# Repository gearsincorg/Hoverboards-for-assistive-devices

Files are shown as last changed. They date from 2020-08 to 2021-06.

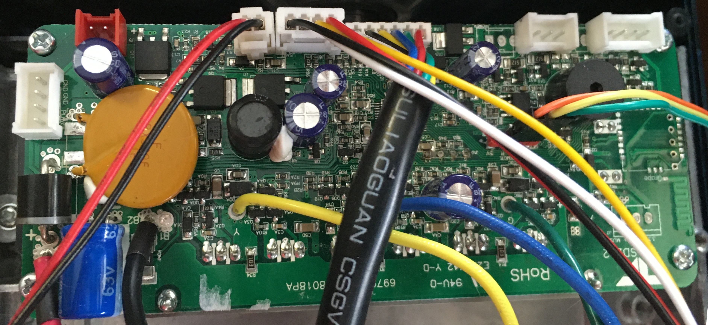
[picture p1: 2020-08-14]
Hoverboard/Documents/MasterBoard.jpg

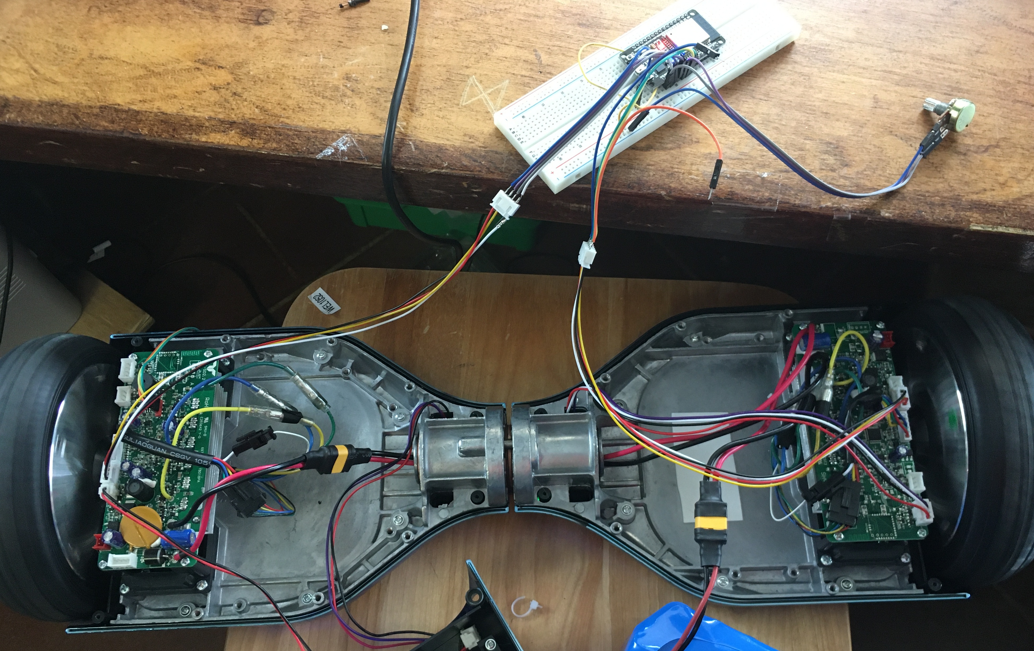
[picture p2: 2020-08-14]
Hoverboard/Documents/Prototype1.jpg

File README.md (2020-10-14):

### Hoverboards for Assistive Devices (HAD) 
By: Phil Malone

Project page:  https://hackaday.io/project/170932-hoverboards-for-assistive-devices

### Purpose:
The HAD project goal is to enable Hoverboards, or Hoverboard drive components to be re-purposed to provide low-cost mobility for assistive devices.

### Components:
The following components are part of this project:

Hoverboard  This is Hoverboard firmware that supports HUGS (Hoverboard Universal Gateway System).  HUGS is new firmware that is loaded into a hoverboard to replace the tilt-based drive system with a command driven velocity system.  HUGS provides a documented command/response protocol whereby commands can be issued to single or dual drive conteollers.

BluJoy-PCB (Bluetooth Joystick PCB).  BluJoy-PCB is a custom two-part Circuit board with PIC microcontroller and two Bluetooth module.  Once sepparated, the two boards enables the Hoverboard to be controlled by a joystick, over a dedicated Bluetooth interface.  

BluJoy.X (Bluetooth Joystick Firmware). BluJoy.X is a custom MPLAB.X program loaded into the PIC processor on the BluJoy PCB.  It performs automatic Bluetooth pairing, and joystick command transmission.  The firmware currently supports microswitch based joysticks, but will be augmented for Potentiometer based joysticks soon.

HUGS-ESP32 This is developmental code for an ESP32 Dev-kit that was used to test and evaluate the HUGS firmware on the Hoverboard. It connects to a wired joystick to generate commands for both Motor Controllers.  It has been superceeded by the BluJoy PIC firmware which communicates through a single Serial port on the Master Motor Controller.

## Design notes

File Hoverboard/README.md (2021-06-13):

### Hoverboard Utility Gateway System (HUGS).

Based on: Hoverboard-Firmware-Hack-Gen2

Hackaday Project Page: https://hackaday.io/project/170932-hoverboards-for-assistive-devices

### Purpose:
The HUGS project goal is to enable Hoverboards, or Hoverboard drive components to be re-purposed to provide low-cost mobility to other systems, such as assistive devices for the disabled, general purpose robots or other labor saving devices.
To implement this goal, new code will be developed and installed in existing hoverboards, to provide a generic purpose control protocol.  This protocol will be used by external devices to run one or more “hoverboard” type wheels.  

### Updated to use new Giga Device Libraries: (3.2) and latest KEIL release (as of 6/13/2021)

### Latest release:
A major modification to the base control strategy was adding several different motor control methods.

The basic method is a simple PWM power control where the the user requests a PWM level from 0 to 1000 and the comutation happens as required by the current sensed position.  The resulting speed is an open loop response.

The next method was a closed loop response using the resultant phase transition speed as feedback. A Feed forward control loop with proportional and integral gain was created to regulate the resulting speed.  Control input is an actual linear speed in the +/- 5MPS range, expressed in mmPS.

The third method is a low speed closed loop mode that uses a sinusoidal stepper motor sequence to drive the commutation at a fixed rate, depending on the requested speed.  The method optains higgly accurate speeds at rates less than about 200 mmPS.

The fourth and final mode is a hybrid of the last two which switches automatically between the low speed stepper mode and the PID control mode.

### Background:
The popular “Hoverboard” toy uses a somewhat unique drive system.  A powerful brushless DC motor has been integrated inside each of the small rubber wheels, and paired with a low cost motor controller.  This mechanical/electrical combination provides a compact drive system that produce precise motions, under considerable load, for relatively low cost.

Through reverse engineering the controller electronics and firmware, code is now available which can be modified to provide alternative operation of the drive system (no longer tied to a tilt-and-drive control system).

The goal of HUGS is to reprogram the motor controller to accept external control commands, and return wheel status information.  HUGS will permit individual wheels to be commanded to run at set speeds, and to move to specified positions.  Current speed and position information will be returned.
By providing an open control protocol, other groups can develop their own high level control logic to run the drive wheels for a myriad of applications.

This repo contains open source firmware that has been deveoped and tested on HOVER-1 Ultra Hoverboard

---

#### Hardware
My initial Hoverboard purchase was the Hover-1 Ultra.  I wanted to do the work on a board that could be purchased by name.
I chose this model because it looked like the company had several models and was likely to be a more reliable vendor than most "direct from China" vendors.

Ultimately my choice backfired on me because instead of the more common single board controller, this unit had two boards (one master and one slave).  So I had to work from a more limited development set of Gen2 hoverboard.

My most upsetting discovery was that when I was all done, I purchased a different model (Maverick vs Ultra) from the same supllier, and discovered that the Ultra code does not translate.   

Since I'm realy not able to reverse engineer this new hardware, this my be a throw-away hoverboard.

So "For the record" everything here has been developed on the Hover-1 Ultra unit, and pictures of the controller boards are in the Documentation folder of this repo.

The HOVER-1 Ultra has two sepparate motor controller boards, usually configured as a master and a slave with a USART Serial port passing commands and data back and forth.

There is a sets of pads that can be used to program the processor using a ST-Link/V2.

There is also a set of pads that can be used for a remote monitor /control port.

---

#### Flashing

The firmware is built with Keil (free up to 32KByte). 
To build the firmware, open the Keil project file (includes in repository).

- If the controller boards contain the original firmware, they will need to be unlocked. To do this, use the STM32 ST-LINK Utility.
- To flash the STM32, use the STM32 ST-LINK Utility, or use Keil and run the code in debug mode, which will download the code first.
- Hold the powerbutton while flashing the firmware, as the controller releases the power latch and switches itself off during flashing

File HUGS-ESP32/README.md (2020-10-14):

# HUGS Human Machine Interface (HMI) ESP32 module.  (Superceeded)

This code is used to program an ESP32 DEVKIT board to send command packets to a Hoverboard (dual controller type) that has been reprogrammed to communicate using the HUGS Protocol.

The code is built using the Espressif-IDF environment.

This code was originally intended to be used as the primary way to interface to a "dual controller" type hoverboard because the ESP32 can drive two serial ports, as well as the programming interface.
This concept was used to implement a wired joystick controller. The code is fully operation, but it will probably not be further developed.  See below. 

Unfortunately, this approach did not lend itself to a simple wireless joystick interface.

To provide a wireless control (joystick) interface, the HUGs protocol was extended to permit a single serial command to be sent to the master motor controller, which would then forward the appropriate components to the slave motor controller using the standard serial cable that is part of the split controller system.
This means that both drives to be controlled using a single serial interface.  This approach enables a simpler uController to be used to "drive" the Hoverboard, and also permits a simple Bluetooth-Serial module to be used to create a wireless interface.

This approach was developed into the BluJoy controller that is also contained in this repo. This design will ultimately replace both the wireless and wires control approach.

For additional information, refer to the Hoverboard Utility Gateway System repo.

https://github.com/gearsincorg/Hoverboard_Utility_Gateway_System

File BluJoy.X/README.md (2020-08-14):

### Hoverboards for Assistive Devices (HAD) 
By: Phil Malone

BluJoy.X is a (Microchip) MPLAB firmware project.
It was created using MPLAB X IDE Version 5.4
It's written in C8 and it makes use of the V3 Code Configurator Module.

The code runs on a PIC16LF18446 processor.  
The '18446 was chosen because it has a serial USART with Configurable Port Pins, and a small quantity of EEPROM memory for storing configuration settings.

I use a PicKit3 to program the processor once it's mounted to the PCB.  

The Firmware is written to run on the BluJoy-PCB which is included as part of this repository.

The code operates in two main modes:

- RUN.	In this mode, the code determines the current joystic configuration from EEPROM, and applies the appropriate speed profiles to the Joystick inputs.  Every 50 mSec, new Axial and Yaw velocities are calculated and sent to the Hoverboard via Bluetooth.

- SETUP.  In this mode, the code reads the device ID's of the two attached Bluetooth modules, and used this information to configure each module to auto-connect with the other module.

To enter the SETUP mode, press and hold both buttons on the PCB for 4 seconds.

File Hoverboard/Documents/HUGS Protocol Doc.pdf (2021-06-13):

HUGS Protocol definition

Revision | Date | Description
Revision | 1.0 | 4/13/2020 Original
2.0 | 5/8/2020 Change to Little Endian.Change to metric speeds. (mm/s)
2.1 | 5/14/2020 Add new Motion Response with Velocity, Position, Power.
2.2 | 7/20/2020 Remove any response for NOR (no response)
3.0 | 1/1/2021 Added new Dual commands to be used by the single debug port on the master.

Note: HUGS uses a binary format, rather than an ASCII character format, so it is not directly printable. Note: All HUGS multi-byte values are sent as little-endian. That is, the LSB is sent first and the MSB sent last.

0 | 1 | 2 | 3 | 4 | 5 | L+4 | L+5 | L+6 | L+7
Send/Rec | BOM | LEN | DEST/SEQ | CMD_ID | RSP_ID | EOM
BOM | Beginning Of Message Character: | Slash | "/"
LEN | Length of variable Data. 0 - 0xF7
DEST/SEQ | LSN (Lower 4 bits) TARGET Identifier. 0-15 | 0x0 = HOST, 0xF = ALL
MSN (Upper 4 bits) Message Sequence. Cycles through 0-15
CMD_ID | On a command, this will be the required action. Indicates how to interpret variable data section
On a response, the CMD_ID will be RSP
RSP_ID | On a command, this is the required Response: Indicates what data should be returned.
On a response, theRSP_ID will be the type of data bing returned in the response.
DATA | Variable number of data bytes . Length defined by LEN parameter
CRC | 16-bit Cyclic Redundancey Check of Bytes 0 to L+4
EOM | End Of Message character: | | Newline | \n 0x0A
Command IDs | Name | Value | LEN
No Operation | NOP | 0x00 | 0
Response | RSP | 0x01 | 0
Reset Pos | RES | 0x02 | 0
Enable | ENA | 0x03 | 0
Disable | DIS | 0x04 | 0
Set Power | POW | 0x05 | 2 | Def 0
Set Speed | SPE | 0x06 | 2 | mm/s (+/- 5000) | Def 0
Set ABS Pos | ABS | 0x07 | 2 | mm (+/- 32767) | Def 0
Set Rel Pos | REL | 0x08 | 2 | mm (+/- 32767) | Def 0
Set Watchdog | DOG | 0x09 | 2 | mS (0-65535) | Def 1000
Set Mode | MOD | 0x0A | 2 | 0,1,2,3 | 0-255mmPs | Def 1,250 | 0=PID,1=STEPPER,2=Hybrid
Set Dual Speed | DSPE | 0x86 | 4 | mm/s (+/- 5000) FW | deg/s (+/- 1425) CW | +=forward, +=clockwise
Power Down | XXX | 0xFF | 0
Response ID | Name | Value | LEN | Data
No Response | NOR | 0x00 | 0
Motion | SMOT | 0x01 | 9 | STATUS | mm/s (+/- 6000) | mm (+/- 2,147,483,648)
Power | SPOW | 0x02 | 3 | STATUS
Velocity | SSPE | 0x03 | 3 | STATUS | mm/s (+/- 6000)
Position | SPOS | 0x04 | 5 | STATUS | mm (+/- 2,147,483,648)
Voltage | SVOL | 0x05 | 3 | STATUS | mV (0-65535)
Current | SAMP | 0x06 | 3 | STATUS | mA (0 65535)
Watchdog | SDOG | 0x07 | 3 | STATUS | mS (0 65535)
PID | SFPI | 0x09 | 7 | STATUS
DualMotion | DSMOT | 0x81 | 13 | STATUS | mm/s (+/- 5000) FW | deg/s (+/- 1425) CW | mm (+/- 2,147,483,648) LEFT WHEEL
Stopped | STOP | 0xFF | 1 | STATUS
STATUS | Bit | 7 | 6 | 5 | 4 | 3 | 2 | 1 | 0
| | | | | | MOD 1 | MOD 0 | Enabled | ESTOP
DATA: LEN Bytes | CRC

+/-1000

+/-1000

F Output | P Output | I Ouput

+/-1000

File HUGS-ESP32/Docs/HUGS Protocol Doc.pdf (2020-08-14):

HUGS Protocol definition

Revision | Date | Description
Revision | 1.0 | 4/13/2020 Original
2.0 | 5/8/2020 Change to Little Endian.Change to metric speeds. (mm/s)
2.1 | 5/14/2020 Add new Motion Response with Velocity, Position, Power.

Note: HUGS uses a binary format, rather than an ASCII character format, so it is not directly printable. Note: All HUGS multi-byte values are sent as little-endian. That is, the LSB is sent first and the MSB sent last.

0 | 1 | 2 | 3 | 4 | 5 | L+4 | L+5 | L+6 | L+7
Send/Rec | BOM | LEN | DEST/SEQ | CMD_ID | RSP_ID | EOM
BOM | Beginning Of Message Character: | Slash | "/"
LEN | Length of variable Data. 0 - 0xF7
DEST/SEQ | LSN (Lower 4 bits) TARGET Identifier. 0-15 | 0x0 = HOST, 0xF = ALL
MSN (Upper 4 bits) Message Sequence. Cycles through 0-15
CMD_ID | On a command, this will be the required action. Indicates how to interpret variable data section
On a response, the CMD_ID will be RSP
RSP_ID | On a command, this is the required Response: Indicates what data should be returned.
On a response, theRSP_ID will be the type of data bing returned in the response.
DATA | Variable number of data bytes . Length defined by LEN parameter
CRC | 16-bit Cyclic Redundancey Check of Bytes 0 to L+4
EOM | End Of Message character: | | Newline | \n 0x0A
Command IDs | Name | Value | LEN
No Operation | NOP | 0x00 | 0
Response | RSP | 0x01 | 0
Enable | ENA | 0x02 | 0
Disable | DIS | 0x03 | 0
Set Power | POW | 0x04 | 2 | Def 0
Set ABS Pos | ABS | 0x05 | 2 | mm (+/- 32767) | Def 0
Set Rel Pos | REL | 0x06 | 2 | mm (+/- 32767) | Def 0
Set Watchdog | DOG | 0x07 | 2 | mS (0-65535) | Def 1000
Reset Pos | RES | 0x08 | 0
Set Speed | SPE | 0x09 | 2 | mm/s (+/- 5000) | Def 0
Set Mode | MOD | 0x0A | 2 | 0,1,2,3 | 0-255mmPs | Def 1,250 | 0=PID,1=STEPPER,2=Hybrid
Power Down | XXX | 0xFF | 0
Response ID | Name | Value | LEN | Data
No Response | NOR | 0x00 | 1 | STATUS
Velocity | SSPE | 0x01 | 3 | STATUS | mm/s (+/- 6000)
Position | SPOS | 0x02 | 5 | STATUS | mm (+/- 2,147,483,648)
Voltage | SVOL | 0x03 | 3 | STATUS | mV (0-65535)
Current | SAMP | 0x04 | 3 | STATUS | mA (0 65535)
Power | SPOW | 0x05 | 3 | STATUS
Watchdog | SDOG | 0x06 | 3 | STATUS | mS (0 65535)
Motion | SMOT | 0x07 | 9 | STATUS | mm/s (+/- 6000) | mm (+/- 2,147,483,648)
Motion | SFPI | 0x08 | 9 | STATUS
Stopped | STOP | 0xFF | 1 | STATUS
STATUS | Bit | 7 | 6 | 5 | 4 | 3 | 2 | 1 | 0
| | | | | | MOD 1 | MOD 0 | Enabled | ESTOP
DATA: LEN Bytes | CRC

+/-1000

+/-1000

F Output | P Output | I Ouput

+/-1000

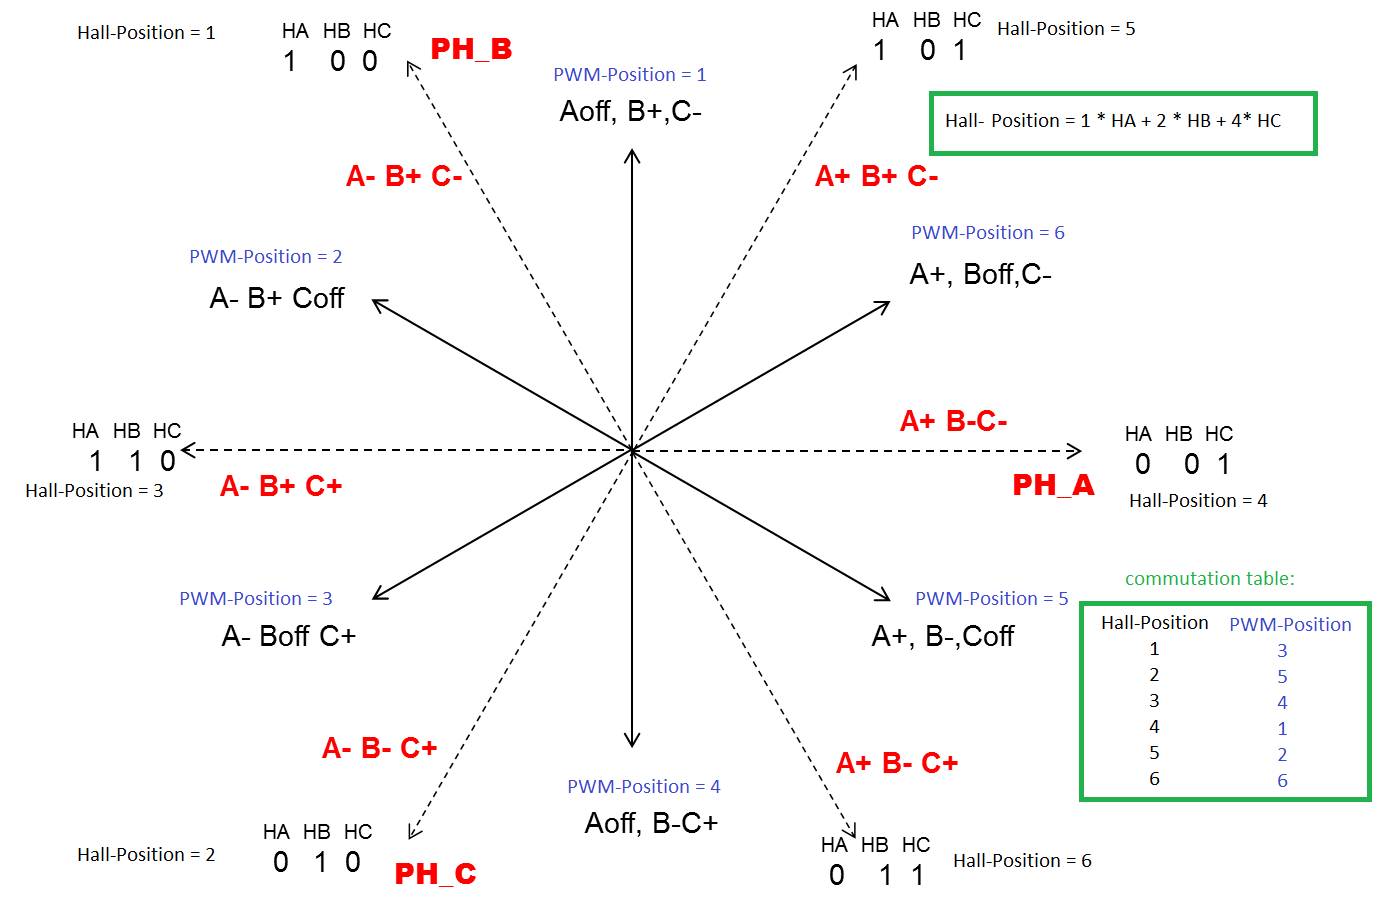
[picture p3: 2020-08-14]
Hoverboard/Documents/BLDC Motor Quadrant Diagram.png

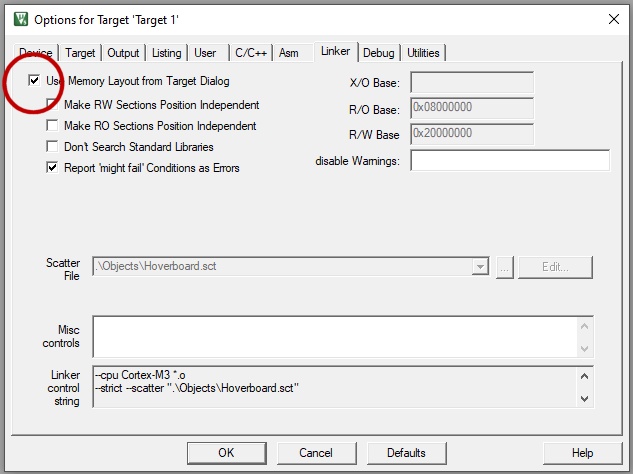
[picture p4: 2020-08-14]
Hoverboard/Documents/LinkerOptions.jpg

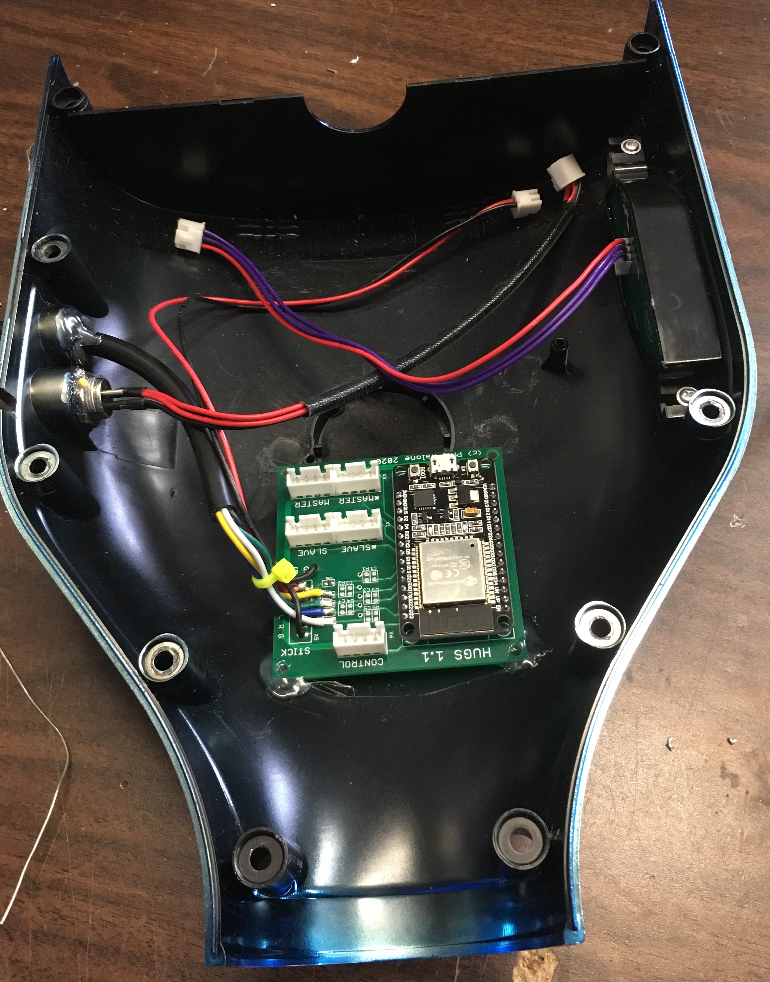
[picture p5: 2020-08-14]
Hoverboard/Documents/Prototype3.jpg

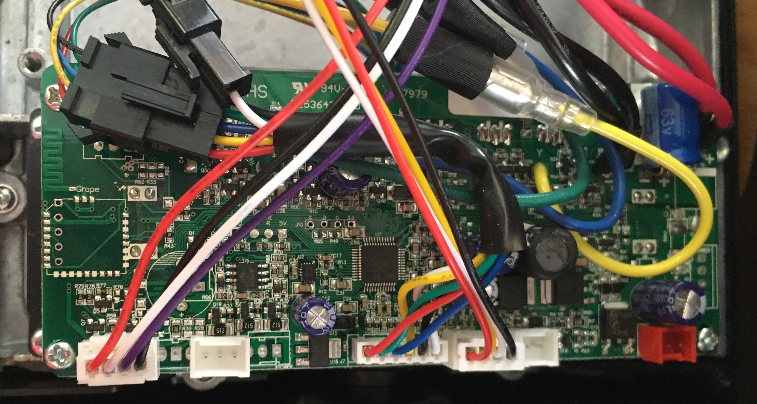
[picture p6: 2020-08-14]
Hoverboard/Documents/SlaveBoard.jpg

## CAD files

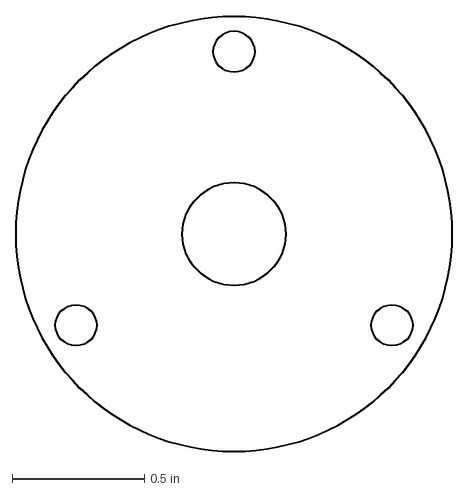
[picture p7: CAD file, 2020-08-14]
Parts/HOVER-disk-b.dxf
1.65 x 1.65 in

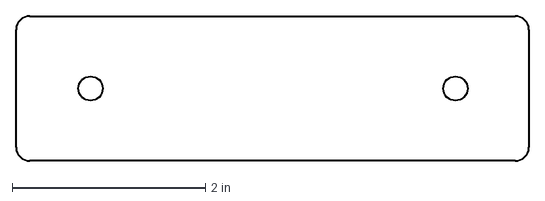
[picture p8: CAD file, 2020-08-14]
Parts/HOVER_plate-b.dxf
5.31 x 1.50 in

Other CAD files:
Parts/HOVER-disk-b.ipt
Parts/HOVER-plate-b.ipt

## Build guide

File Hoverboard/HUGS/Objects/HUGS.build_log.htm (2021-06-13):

µVision Build Log

Tool Versions:

IDE-Version: µVision V5.34.0.0
Copyright (C) 2021 ARM Ltd and ARM Germany GmbH. All rights reserved.
License Information: Philip Malone, GEARS, LIC=----
 
Tool Versions:
Toolchain:       MDK-Lite  Version: 5.34.0.0
Toolchain Path:  C:\Keil_v5\ARM\ARMCC\Bin
C Compiler:      Armcc.exe V5.06 update 7 (build 960)
Assembler:       Armasm.exe V5.06 update 7 (build 960)
Linker/Locator:  ArmLink.exe V5.06 update 7 (build 960)
Library Manager: ArmAr.exe V5.06 update 7 (build 960)
Hex Converter:   FromElf.exe V5.06 update 7 (build 960)
CPU DLL:         SARMCM3.DLL V5.34.0.0
Dialog DLL:      DCM.DLL V1.17.3.0
Target DLL:      STLink\ST-LINKIII-KEIL_SWO.dll V3.0.8.0
Dialog DLL:      TCM.DLL V1.48.0.0

Project:

D:\Users\Phil\GitHub\Hoverboard_Utility_Gateway_System\HUGS\HUGS.uvprojx
Project File Date:  06/13/2021

Output:

*** Using Compiler 'V5.06 update 7 (build 960)', folder: 'C:\Keil_v5\ARM\ARMCC\Bin'
Build target 'Target 1'
compiling main.c...
compiling it.c...
compiling led.c...
compiling comms.c...
compiling commsSteering.c...
compiling gd32f1x0_adc.c...
compiling gd32f1x0_dbg.c...
compiling commsHUGS.c...
compiling gd32f1x0_dma.c...
compiling setup.c...
compiling bldc.c...
compiling gd32f1x0_opa.c...
assembling startup_gd32f1x0.s...
compiling gd32f1x0_fwdgt.c...
compiling gd32f1x0_gpio.c...
compiling gd32f1x0_pmu.c...
compiling gd32f1x0_misc.c...
compiling gd32f1x0_i2c.c...
compiling gd32f1x0_syscfg.c...
compiling gd32f1x0_wwdgt.c...
compiling gd32f1x0_rcu.c...
compiling gd32f1x0_usart.c...
compiling gd32f1x0_timer.c...
compiling system_gd32f1x0.c...
linking...
Program Size: Code=20668 RO-data=1168 RW-data=160 ZI-data=2320  
FromELF: creating hex file...
".\Objects\HUGS.axf" - 0 Error(s), 0 Warning(s).

Software Packages used:

Package Vendor: ARM
                http://www.keil.com/pack/ARM.CMSIS.5.7.0.pack
                ARM.CMSIS.5.7.0
                CMSIS (Cortex Microcontroller Software Interface Standard)
   * Component: CORE Version: 5.4.0

Package Vendor: GigaDevice
                http://gd32mcu.com/data/documents/pack/GigaDevice.GD32F1x0_DFP.3.2.0.pack
                GigaDevice.GD32F1x0_DFP.3.2.0
                GigaDevice GD32F1x0 Series Device Support and Examples
   * Component: ADC Version: 3.2.0
   * Component: DMA Version: 3.2.0
   * Component: FWDGT Version: 3.2.0
   * Component: GPIO Version: 3.2.0
   * Component: I2C Version: 3.2.0
   * Component: MCUDBG Version: 3.2.0
   * Component: MISC Version: 3.2.0
   * Component: OPA Version: 3.2.0
   * Component: PMU Version: 3.2.0
   * Component: RCU Version: 3.2.0
   * Component: SYSCFG Version: 3.2.0
   * Component: TIMER Version: 3.2.0
   * Component: USART Version: 3.2.0
   * Component: WWDGT Version: 3.2.0
   * Component: GD32F1x0_libopt Version: 3.2.0
   * Component: Startup Version: 3.2.0

Collection of Component include folders:

  .\RTE\_Target_1
  C:\Users\13015\AppData\Local\Arm\Packs\ARM\CMSIS\5.7.0\CMSIS\Core\Include
  C:\Users\13015\AppData\Local\Arm\Packs\GigaDevice\GD32F1x0_DFP\3.2.0\Device\Firmware\Peripherals\inc
  C:\Users\13015\AppData\Local\Arm\Packs\GigaDevice\GD32F1x0_DFP\3.2.0\Device\Include

Collection of Component Files used:

   * Component: ARM::CMSIS:CORE:5.4.0

   * Component: GigaDevice::Device:GD32F1x0_StdPeripherals:ADC:3.2.0
      Source file:   Device\Firmware\Peripherals\src\gd32f1x0_adc.c
      Include file:  Device\Firmware\Peripherals\inc\gd32f1x0_adc.h

   * Component: GigaDevice::Device:GD32F1x0_StdPeripherals:DMA:3.2.0
      Source file:   Device\Firmware\Peripherals\src\gd32f1x0_dma.c
      Include file:  Device\Firmware\Peripherals\inc\gd32f1x0_dma.h

   * Component: GigaDevice::Device:GD32F1x0_StdPeripherals:FWDGT:3.2.0
      Include file:  Device\Firmware\Peripherals\inc\gd32f1x0_fwdgt.h
      Source file:   Device\Firmware\Peripherals\src\gd32f1x0_fwdgt.c

   * Component: GigaDevice::Device:GD32F1x0_StdPeripherals:GPIO:3.2.0
      Include file:  Device\Firmware\Peripherals\inc\gd32f1x0_gpio.h
      Source file:   Device\Firmware\Peripherals\src\gd32f1x0_gpio.c

   * Component: GigaDevice::Device:GD32F1x0_StdPeripherals:I2C:3.2.0
      Source file:   Device\Firmware\Peripherals\src\gd32f1x0_i2c.c
      Include file:  Device\Firmware\Peripherals\inc\gd32f1x0_i2c.h

   * Component: GigaDevice::Device:GD32F1x0_StdPeripherals:MCUDBG:3.2.0
      Source file:   Device\Firmware\Peripherals\src\gd32f1x0_dbg.c
      Include file:  Device\Firmware\Peripherals\inc\gd32f1x0_dbg.h

   * Component: GigaDevice::Device:GD32F1x0_StdPeripherals:MISC:3.2.0
      Source file:   Device\Firmware\Peripherals\src\gd32f1x0_misc.c
      Include file:  Device\Firmware\Peripherals\inc\gd32f1x0_misc.h

   * Component: GigaDevice::Device:GD32F1x0_StdPeripherals:OPA:3.2.0
      Include file:  Device\Firmware\Peripherals\inc\gd32f1x0_opa.h
      Source file:   Device\Firmware\Peripherals\src\gd32f1x0_opa.c

   * Component: GigaDevice::Device:GD32F1x0_StdPeripherals:PMU:3.2.0
      Include file:  Device\Firmware\Peripherals\inc\gd32f1x0_pmu.h
      Source file:   Device\Firmware\Peripherals\src\gd32f1x0_pmu.c

   * Component: GigaDevice::Device:GD32F1x0_StdPeripherals:RCU:3.2.0
      Include file:  Device\Firmware\Peripherals\inc\gd32f1x0_rcu.h
      Source file:   Device\Firmware\Peripherals\src\gd32f1x0_rcu.c

   * Component: GigaDevice::Device:GD32F1x0_StdPeripherals:SYSCFG:3.2.0
      Include file:  Device\Firmware\Peripherals\inc\gd32f1x0_syscfg.h
      Source file:   Device\Firmware\Peripherals\src\gd32f1x0_syscfg.c

   * Component: GigaDevice::Device:GD32F1x0_StdPeripherals:TIMER:3.2.0
      Include file:  Device\Firmware\Peripherals\inc\gd32f1x0_timer.h
      Source file:   Device\Firmware\Peripherals\src\gd32f1x0_timer.c

   * Component: GigaDevice::Device:GD32F1x0_StdPeripherals:USART:3.2.0
      Source file:   Device\Firmware\Peripherals\src\gd32f1x0_usart.c
      Include file:  Device\Firmware\Peripherals\inc\gd32f1x0_usart.h

   * Component: GigaDevice::Device:GD32F1x0_StdPeripherals:WWDGT:3.2.0
      Source file:   Device\Firmware\Peripherals\src\gd32f1x0_wwdgt.c
      Include file:  Device\Firmware\Peripherals\inc\gd32f1x0_wwdgt.h

   * Component: GigaDevice::Device:GD32F1x0_libopt:3.2.0
      Include file:  Device\Include\gd32f1x0_libopt.h

   * Component: GigaDevice::Device:Startup:3.2.0
      Include file:  Device\Include\gd32f1x0.h
      Source file:   Device\Source\startup_gd32f1x0.s
      Source file:   Device\Source\system_gd32f1x0.c
Build Time Elapsed:  00:00:01

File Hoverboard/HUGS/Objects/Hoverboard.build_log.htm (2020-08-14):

µVision Build Log

Tool Versions:

IDE-Version: µVision V5.29.0.0
Copyright (C) 2019 ARM Ltd and ARM Germany GmbH. All rights reserved.
License Information: Phil Malone, Mr. Phil, LIC=----
 
Tool Versions:
Toolchain:       MDK-Lite  Version: 5.29.0.0
Toolchain Path:  d:\Keil_v5\ARM\ARMCC\Bin
C Compiler:      Armcc.exe V5.06 update 6 (build 750)
Assembler:       Armasm.exe V5.06 update 6 (build 750)
Linker/Locator:  ArmLink.exe V5.06 update 6 (build 750)
Library Manager: ArmAr.exe V5.06 update 6 (build 750)
Hex Converter:   FromElf.exe V5.06 update 6 (build 750)
CPU DLL:         SARMCM3.DLL V5.29.0.0
Dialog DLL:      DCM.DLL V1.17.3.0
Target DLL:      UL2CM3.DLL V1.163.0.0
Dialog DLL:      TCM.DLL V1.36.5.0

Project:

D:\Users\Phil\GitHub\HUGS\HUGS\HUGS.uvprojx
Project File Date:  02/19/2020

Output:

*** Using Compiler 'V5.06 update 6 (build 750)', folder: 'd:\Keil_v5\ARM\ARMCC\Bin'
Build target 'Target 1'
compiling main.c...
Src\main.c(37): error:  #5: cannot open source input file "../Inc/commsBluetooth.h": No such file or directory
  #include "../Inc/commsBluetooth.h"
Src\main.c: 0 warnings, 1 error
compiling setup.c...
compiling bldc.c...
compiling it.c...
Src\it.c(34): error:  #5: cannot open source input file "../Inc/commsBluetooth.h": No such file or directory
  #include "../Inc/commsBluetooth.h"
Src\it.c: 0 warnings, 1 error
compiling comms.c...
compiling commsSteering.c...
compiling commsMasterSlave.c...
compiling led.c...
compiling gd32f1x0_dbg.c...
compiling gd32f1x0_adc.c...
compiling gd32f1x0_dma.c...
compiling gd32f1x0_fwdgt.c...
compiling gd32f1x0_gpio.c...
compiling gd32f1x0_opa.c...
compiling gd32f1x0_i2c.c...
compiling gd32f1x0_misc.c...
compiling gd32f1x0_pmu.c...
compiling gd32f1x0_rcu.c...
compiling gd32f1x0_syscfg.c...
compiling gd32f1x0_timer.c...
compiling gd32f1x0_wwdgt.c...
compiling gd32f1x0_usart.c...
assembling startup_gd32f1x0.s...
compiling system_gd32f1x0.c...
".\Objects\Hoverboard.axf" - 2 Error(s), 0 Warning(s).

Software Packages used:

Package Vendor: ARM
                http://www.keil.com/pack/ARM.CMSIS.5.6.0.pack
                ARM.CMSIS.5.6.0
                CMSIS (Cortex Microcontroller Software Interface Standard)
   * Component: CORE Version: 5.3.0

Package Vendor: GigaDevice
                http://gd32mcu.21ic.com/data/documents/yingyongruanjian/GigaDevice.GD32F1x0_DFP.3.1.1.pack
                GigaDevice.GD32F1x0_DFP.3.1.1
                GigaDevice GD32F1x0 Series Device Support and Examples
   * Component: ADC Version: 3.1.0
   * Component: DMA Version: 3.1.0
   * Component: FWDGT Version: 3.1.0
   * Component: GPIO Version: 3.1.0
   * Component: I2C Version: 3.1.0
   * Component: MCUDBG Version: 3.1.0
   * Component: MISC Version: 3.1.0
   * Component: OPA Version: 3.1.0
   * Component: PMU Version: 3.1.0
   * Component: RCU Version: 3.1.0
   * Component: SYSCFG Version: 3.1.0
   * Component: TIMER Version: 3.1.0
   * Component: USART Version: 3.1.0
   * Component: WWDGT Version: 3.1.0
   * Component: GD32F1x0_libopt Version: 3.1.0
   * Component: Startup Version: 3.1.0

Collection of Component include folders:

  .\RTE\_Target_1
  d:\Users\Phil\AppData\Local\Arm\Packs\ARM\CMSIS\5.6.0\CMSIS\Core\Include
  d:\Users\Phil\AppData\Local\Arm\Packs\GigaDevice\GD32F1x0_DFP\3.1.1\Device\Firmware\Peripherals\inc
  d:\Users\Phil\AppData\Local\Arm\Packs\GigaDevice\GD32F1x0_DFP\3.1.1\Device\Include

Collection of Component Files used:

   * Component: ARM::CMSIS:CORE:5.3.0

   * Component: GigaDevice::Device:GD32F1x0_StdPeripherals:ADC:3.1.0
      Include file:  Device\Firmware\Peripherals\inc\gd32f1x0_adc.h
      Source file:   Device\Firmware\Peripherals\src\gd32f1x0_adc.c

   * Component: GigaDevice::Device:GD32F1x0_StdPeripherals:DMA:3.1.0
      Source file:   Device\Firmware\Peripherals\src\gd32f1x0_dma.c
      Include file:  Device\Firmware\Peripherals\inc\gd32f1x0_dma.h

   * Component: GigaDevice::Device:GD32F1x0_StdPeripherals:FWDGT:3.1.0
      Source file:   Device\Firmware\Peripherals\src\gd32f1x0_fwdgt.c
      Include file:  Device\Firmware\Peripherals\inc\gd32f1x0_fwdgt.h

   * Component: GigaDevice::Device:GD32F1x0_StdPeripherals:GPIO:3.1.0
      Source file:   Device\Firmware\Peripherals\src\gd32f1x0_gpio.c
      Include file:  Device\Firmware\Peripherals\inc\gd32f1x0_gpio.h

   * Component: GigaDevice::Device:GD32F1x0_StdPeripherals:I2C:3.1.0
      Source file:   Device\Firmware\Peripherals\src\gd32f1x0_i2c.c
      Include file:  Device\Firmware\Peripherals\inc\gd32f1x0_i2c.h

   * Component: GigaDevice::Device:GD32F1x0_StdPeripherals:MCUDBG:3.1.0
      Include file:  Device\Firmware\Peripherals\inc\gd32f1x0_dbg.h
      Source file:   Device\Firmware\Peripherals\src\gd32f1x0_dbg.c

   * Component: GigaDevice::Device:GD32F1x0_StdPeripherals:MISC:3.1.0
      Include file:  Device\Firmware\Peripherals\inc\gd32f1x0_misc.h
      Source file:   Device\Firmware\Peripherals\src\gd32f1x0_misc.c

   * Component: GigaDevice::Device:GD32F1x0_StdPeripherals:OPA:3.1.0
      Include file:  Device\Firmware\Peripherals\inc\gd32f1x0_opa.h
      Source file:   Device\Firmware\Peripherals\src\gd32f1x0_opa.c

   * Component: GigaDevice::Device:GD32F1x0_StdPeripherals:PMU:3.1.0
      Include file:  Device\Firmware\Peripherals\inc\gd32f1x0_pmu.h
      Source file:   Device\Firmware\Peripherals\src\gd32f1x0_pmu.c

   * Component: GigaDevice::Device:GD32F1x0_StdPeripherals:RCU:3.1.0
      Include file:  Device\Firmware\Peripherals\inc\gd32f1x0_rcu.h
      Source file:   Device\Firmware\Peripherals\src\gd32f1x0_rcu.c

   * Component: GigaDevice::Device:GD32F1x0_StdPeripherals:SYSCFG:3.1.0
      Include file:  Device\Firmware\Peripherals\inc\gd32f1x0_syscfg.h
      Source file:   Device\Firmware\Peripherals\src\gd32f1x0_syscfg.c

   * Component: GigaDevice::Device:GD32F1x0_StdPeripherals:TIMER:3.1.0
      Source file:   Device\Firmware\Peripherals\src\gd32f1x0_timer.c
      Include file:  Device\Firmware\Peripherals\inc\gd32f1x0_timer.h

   * Component: GigaDevice::Device:GD32F1x0_StdPeripherals:USART:3.1.0
      Include file:  Device\Firmware\Peripherals\inc\gd32f1x0_usart.h
      Source file:   Device\Firmware\Peripherals\src\gd32f1x0_usart.c

   * Component: GigaDevice::Device:GD32F1x0_StdPeripherals:WWDGT:3.1.0
      Include file:  Device\Firmware\Peripherals\inc\gd32f1x0_wwdgt.h
      Source file:   Device\Firmware\Peripherals\src\gd32f1x0_wwdgt.c

   * Component: GigaDevice::Device:GD32F1x0_libopt:3.1.0
      Include file:  Device\Include\gd32f1x0_libopt.h

   * Component: GigaDevice::Device:Startup:3.1.0
      Source file:   Device\Source\startup_gd32f1x0.s
      Source file:   Device\Source\system_gd32f1x0.c
      Include file:  Device\Include\gd32f1x0.h
Target not created.
Build Time Elapsed:  00:00:04

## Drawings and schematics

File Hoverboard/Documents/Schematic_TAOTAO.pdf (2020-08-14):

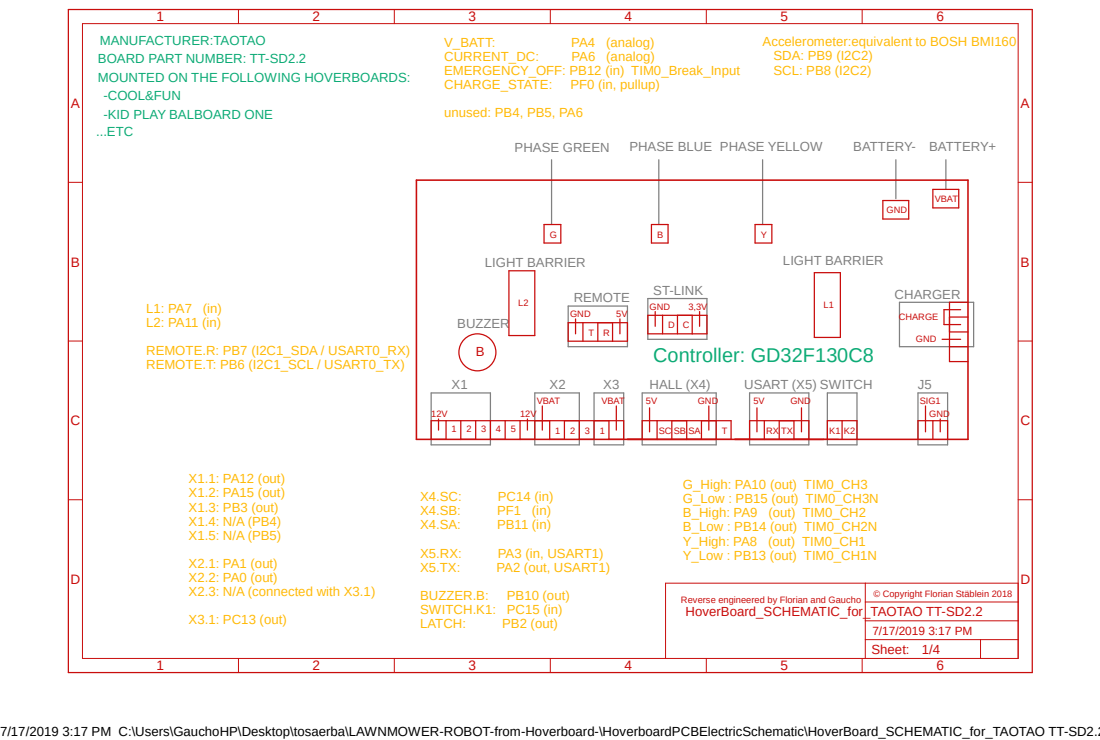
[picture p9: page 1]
HALL (X4); USART (X5) SWITCH; REMOTE; ST-LINK; CHARGER; PHASE GREEN; PHASE BLUE PHASE YELLOW; LIGHT BARRIER; BATTERY- BATTERY+; BUZZER; VBAT; GND; SIG1 GND; CHARGE; Sheet:; Controller: GD32F130C8; X1.1: PA12 (out) X1.2: PA15 (out) X1.3: PB3 (out) X1.4: N/A (PB4) X1.5: N/A (PB5); X2.1: PA1 (out) X2.2: PA0 (out) X2.3: N/A (connected with X3.1); X3.1: PC13 (out); PA3 (in, USART1); PA2 (out, USART1); BUZZER.B:; PB10 (out); SWITCH.K1: PC15 (in); LATCH:; PB2 (out)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

MANUFACTURER:TAOTAO
BOARD PART NUMBER: TT-SD2.2
MOUNTED ON THE FOLLOWING HOVERBOARDS:
-COOL&FUN
-KID PLAY BALBOARD ONE
...ETC

Accelerometer:equivalent to BOSH BMI160
SDA: PB9 (I2C2)
SCL: PB8 (I2C2)

© Copyright Florian Stäblein 2018

Reverse engineered by Florian and Gaucho
HoverBoard_SCHEMATIC_for_TAOTAO TT-SD2.2

7/17/2019 3:17 PM C:\Users\GauchoHP\Desktop\tosaerba\LAWNMOWER-ROBOT-from-Hoverboard-\HoverboardPCBElectricSchematic\HoverBoard_SCHEMATIC_for_TAOTAO TT-SD2.2.sch (Sheet: 1/4)

## HALL

## USART

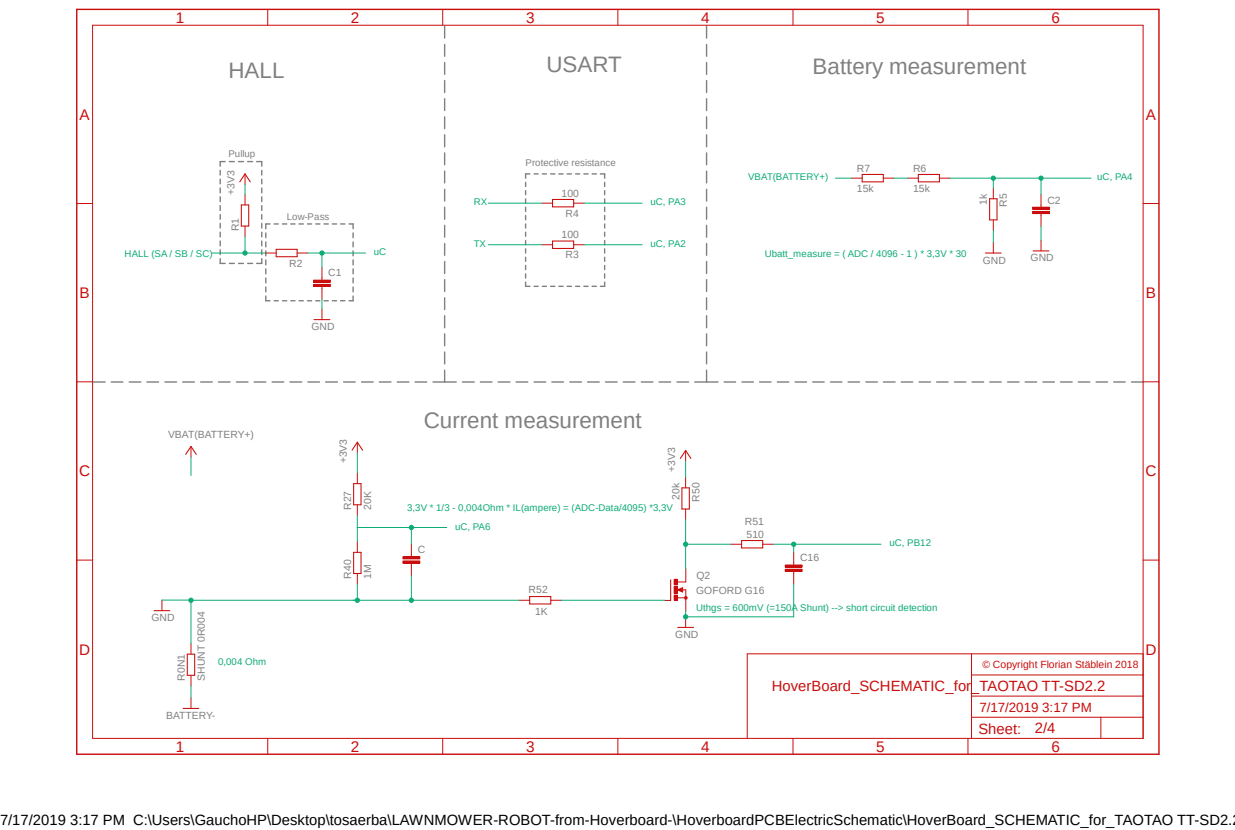
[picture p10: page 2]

3,3V * 1/3 - 0,004Ohm * IL(ampere) = (ADC-Data/4095) *3,3V

GOFORD G16
Uthgs = 600mV (=150A Shunt) --> short circuit detection

7/17/2019 3:17 PM C:\Users\GauchoHP\Desktop\tosaerba\LAWNMOWER-ROBOT-from-Hoverboard-\HoverboardPCBElectricSchematic\HoverBoard_SCHEMATIC_for_TAOTAO TT-SD2.2.sch (Sheet: 2/4)

X1-1 | X1-2 | X1-3 | X1-4

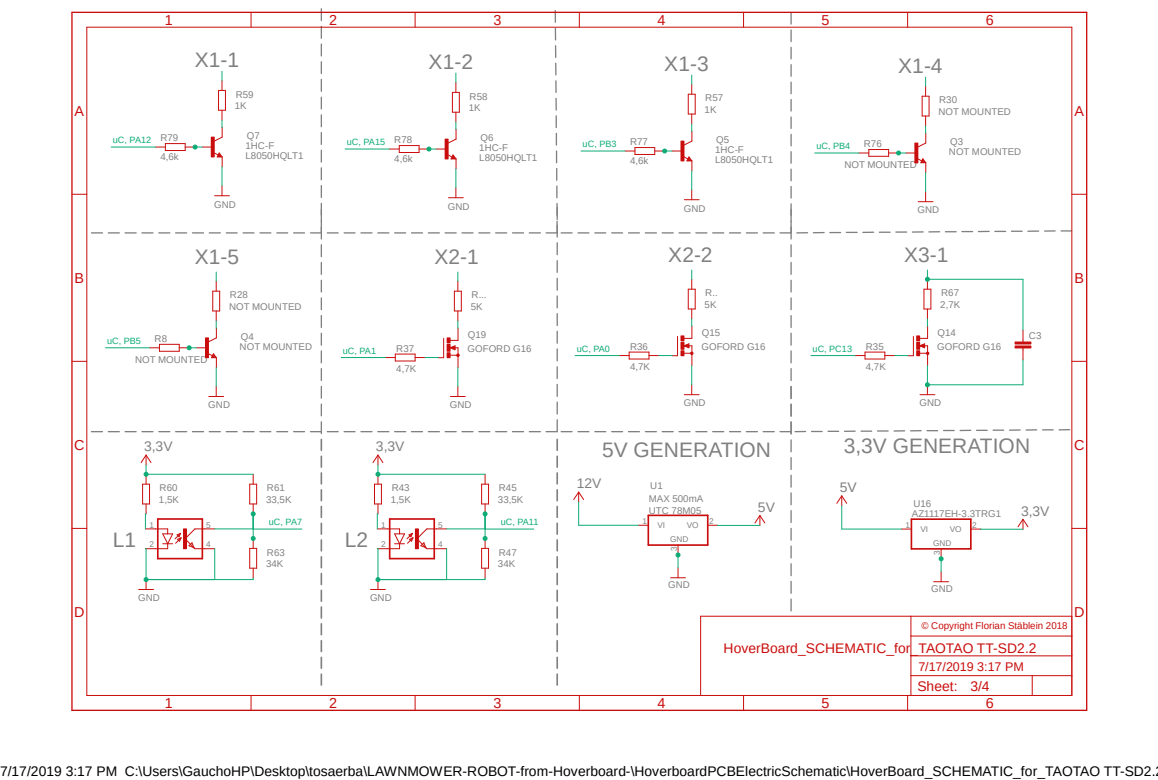
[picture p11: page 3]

7/17/2019 3:17 PM C:\Users\GauchoHP\Desktop\tosaerba\LAWNMOWER-ROBOT-from-Hoverboard-\HoverboardPCBElectricSchematic\HoverBoard_SCHEMATIC_for_TAOTAO TT-SD2.2.sch (Sheet: 3/4)

## CHARGER INPUT

## "REMOTE" SERIAL PORT

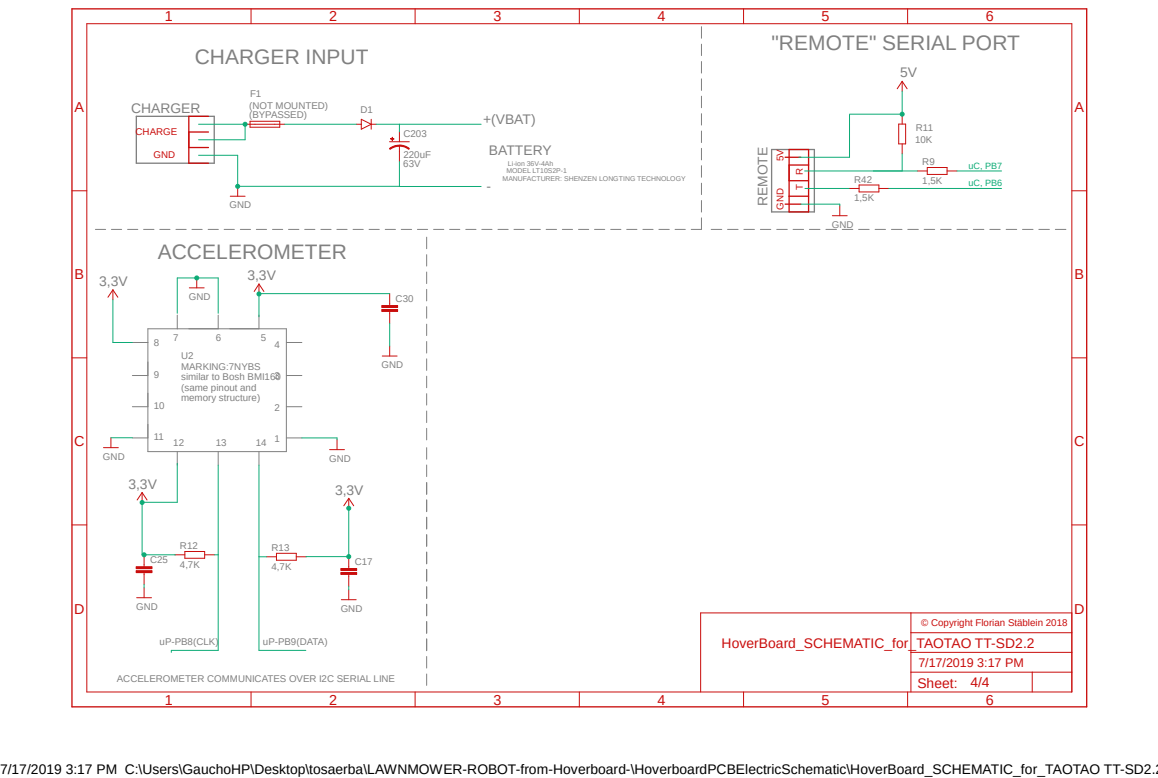
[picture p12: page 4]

MANUFACTURER: SHENZEN LONGTING TECHNOLOGY GND

ACCELEROMETER COMMUNICATES OVER I2C SERIAL LINE

7/17/2019 3:17 PM C:\Users\GauchoHP\Desktop\tosaerba\LAWNMOWER-ROBOT-from-Hoverboard-\HoverboardPCBElectricSchematic\HoverBoard_SCHEMATIC_for_TAOTAO TT-SD2.2.sch (Sheet: 4/4)

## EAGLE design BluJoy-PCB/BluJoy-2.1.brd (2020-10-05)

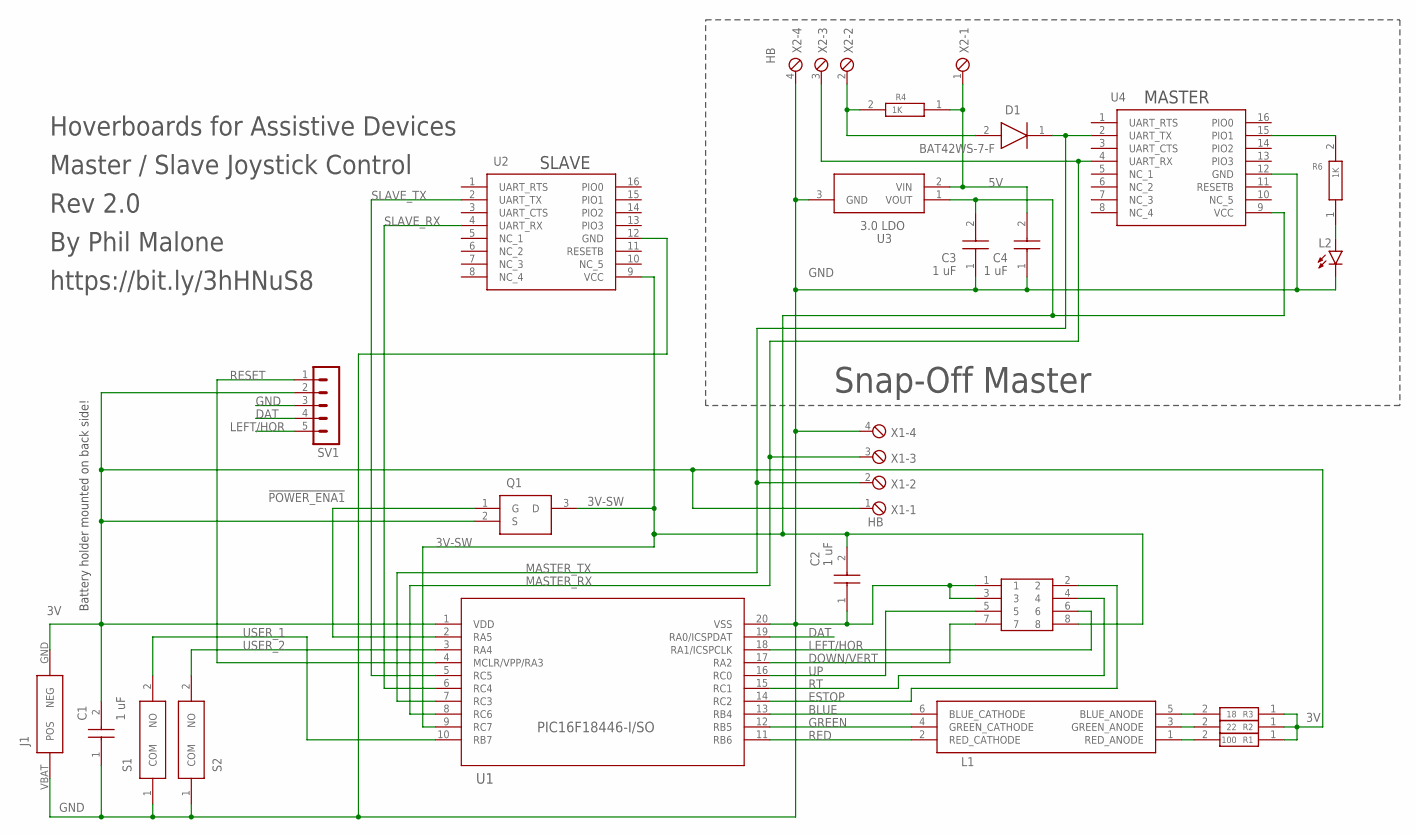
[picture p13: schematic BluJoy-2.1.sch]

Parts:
C1, C2, C3, C4: 1 uF; CAPC1608X90N
D1: BAT42WS-7-F; SOD2513X120N
J1: 2468
J2: PHOENIX3.5X8-B; 1751303
L1: ASMB-TTF0-0A20B; ASMBTTF00A20B
L2: LEDCHIP-LED0603; CHIP-LED0603
Q1: P-FET; SOT96P237X111-3N
R1: 100; RESC1608X50N
R2: 22; RESC1608X50N
R3: 18; RESC1608X50N
R4, R6: 1K; RESC1608X50N
S1, S2: PTS636_SK25J_SMTR_LFS; PTS636SK25JSMTRLFS
SV1: PICKIT; MA05-1
U1: PIC16F18446-I/SO; SOIC20_SO_MCH
U2, U4: HM-11; HM-11-MODULE
U3: 3.0 LDO; SOT95P237X112-3N
X1, X2: HB; 4POL254

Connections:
3V: C1.2 (C2), J1.GND (NEG), Q1.2 (S), R1.1, R2.1, R3.1, SV1.2, U1.1 (VDD), X1.1
3V-SW: C2.2 (C2), C3.2 (C2), J2.8, Q1.3 (D), U1.9 (RC7), U2.9 (VCC), U3.1 (VOUT), U4.9 (VCC)
5V: C4.2 (C2), R4.1, U3.2 (VIN), X2.1
!POWER_ENA1: Q1.1 (G), U1.2 (RA5)
BLUE: L1.6 (BLUE_CATHODE), U1.13 (RB4)
DAT: SV1.4, U1.19 (RA0/ICSPDAT)
DOWN/VERT: J2.7, U1.17 (RA2)
ESTOP: J2.2, U1.14 (RC2)
GND: C1.1 (C1), C2.1 (C1), C3.1 (C1), C4.1 (C1), J1.VBAT (POS), J2.1, J2.3, L2.C, S1.1 (COM), S2.1 (COM), SV1.3, U1.20 (VSS), U2.12 (GND), U3.3 (GND), U4.12 (GND), X1.4, X2.4
GREEN: L1.4 (GREEN_CATHODE), U1.12 (RB5)
LEFT/HOR: J2.6, SV1.5, U1.18 (RA1/ICSPCLK)
MASTER_RX: U1.8 (RC6), U4.4 (UART_RX), X1.3, X2.3
MASTER_TX: D1.1 (K), U1.7 (RC3), U4.2 (UART_TX), X1.2
unnamed: D1.2 (A), R4.2, X2.2
unnamed: R6.2, U4.15 (PIO1)
unnamed: L2.A, R6.1
unnamed: L1.1 (RED_ANODE), R1.2
unnamed: L1.3 (GREEN_ANODE), R2.2
unnamed: L1.5 (BLUE_ANODE), R3.2
RED: L1.2 (RED_CATHODE), U1.11 (RB6)
RESET: SV1.1, U1.4 (MCLR/VPP/RA3)
RT: J2.4, U1.15 (RC1)
SLAVE_RX: U1.6 (RC4), U2.4 (UART_RX)
SLAVE_TX: U1.5 (RC5), U2.2 (UART_TX)
UP: J2.5, U1.16 (RC0)
USER_1: S1.2 (NO), U1.10 (RB7)
USER_2: S2.2 (NO), U1.3 (RA4)

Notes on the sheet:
Snap-Off Master
MASTER
SLAVE
Hoverboards for Assistive Devices
Master / Slave Joystick Control
Rev 2.0
By Phil Malone
https://bit.ly/3hHNuS8
Battery holder mounted on back side!

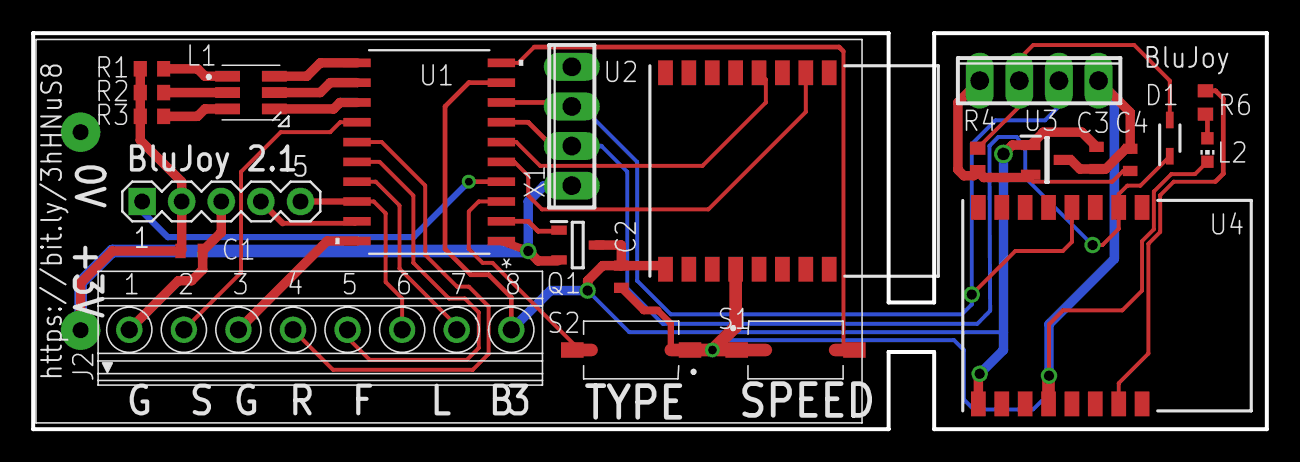
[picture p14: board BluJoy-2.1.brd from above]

Board: 2 copper layers, 79.1 x 25.4 mm, 24 parts (0 on the bottom side), 27 nets.

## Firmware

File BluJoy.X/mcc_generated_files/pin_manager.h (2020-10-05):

/**
  @Generated Pin Manager Header File

  @Company:
    Microchip Technology Inc.

  @File Name:
    pin_manager.h

  @Summary:
    This is the Pin Manager file generated using PIC10 / PIC12 / PIC16 / PIC18 MCUs

  @Description
    This header file provides APIs for driver for .
    Generation Information :
        Product Revision  :  PIC10 / PIC12 / PIC16 / PIC18 MCUs - 1.81.4
        Device            :  PIC16LF18446
        Driver Version    :  2.11
    The generated drivers are tested against the following:
        Compiler          :  XC8 2.20 and above
        MPLAB 	          :  MPLAB X 5.40	
*/

/*
    (c) 2018 Microchip Technology Inc. and its subsidiaries. 
    
    Subject to your compliance with these terms, you may use Microchip software and any 
    derivatives exclusively with Microchip products. It is your responsibility to comply with third party 
    license terms applicable to your use of third party software (including open source software) that 
    may accompany Microchip software.
    
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
    IN NO EVENT WILL MICROCHIP BE LIABLE FOR ANY INDIRECT, SPECIAL, PUNITIVE, 
    INCIDENTAL OR CONSEQUENTIAL LOSS, DAMAGE, COST OR EXPENSE OF ANY KIND 
    WHATSOEVER RELATED TO THE SOFTWARE, HOWEVER CAUSED, EVEN IF MICROCHIP 
    HAS BEEN ADVISED OF THE POSSIBILITY OR THE DAMAGES ARE FORESEEABLE. TO 
    THE FULLEST EXTENT ALLOWED BY LAW, MICROCHIP'S TOTAL LIABILITY ON ALL 
    CLAIMS IN ANY WAY RELATED TO THIS SOFTWARE WILL NOT EXCEED THE AMOUNT 
    OF FEES, IF ANY, THAT YOU HAVE PAID DIRECTLY TO MICROCHIP FOR THIS 
    SOFTWARE.
*/

#ifndef PIN_MANAGER_H
#define PIN_MANAGER_H

/**
  Section: Included Files
*/

#include <xc.h>

#define INPUT   1
#define OUTPUT  0

#define HIGH    1
#define LOW     0

#define ANALOG      1
#define DIGITAL     0

#define PULL_UP_ENABLED      1
#define PULL_UP_DISABLED     0

// get/set JSLE aliases
#define JSLE_TRIS                 TRISAbits.TRISA1
#define JSLE_LAT                  LATAbits.LATA1
#define JSLE_PORT                 PORTAbits.RA1
#define JSLE_WPU                  WPUAbits.WPUA1
#define JSLE_OD                   ODCONAbits.ODCA1
#define JSLE_ANS                  ANSELAbits.ANSA1
#define JSLE_SetHigh()            do { LATAbits.LATA1 = 1; } while(0)
#define JSLE_SetLow()             do { LATAbits.LATA1 = 0; } while(0)
#define JSLE_Toggle()             do { LATAbits.LATA1 = ~LATAbits.LATA1; } while(0)
#define JSLE_GetValue()           PORTAbits.RA1
#define JSLE_SetDigitalInput()    do { TRISAbits.TRISA1 = 1; } while(0)
#define JSLE_SetDigitalOutput()   do { TRISAbits.TRISA1 = 0; } while(0)
#define JSLE_SetPullup()          do { WPUAbits.WPUA1 = 1; } while(0)
#define JSLE_ResetPullup()        do { WPUAbits.WPUA1 = 0; } while(0)
#define JSLE_SetPushPull()        do { ODCONAbits.ODCA1 = 0; } while(0)
#define JSLE_SetOpenDrain()       do { ODCONAbits.ODCA1 = 1; } while(0)
#define JSLE_SetAnalogMode()      do { ANSELAbits.ANSA1 = 1; } while(0)
#define JSLE_SetDigitalMode()     do { ANSELAbits.ANSA1 = 0; } while(0)

// get/set JSDO aliases
#define JSDO_TRIS                 TRISAbits.TRISA2
#define JSDO_LAT                  LATAbits.LATA2
#define JSDO_PORT                 PORTAbits.RA2
#define JSDO_WPU                  WPUAbits.WPUA2
#define JSDO_OD                   ODCONAbits.ODCA2
#define JSDO_ANS                  ANSELAbits.ANSA2
#define JSDO_SetHigh()            do { LATAbits.LATA2 = 1; } while(0)
#define JSDO_SetLow()             do { LATAbits.LATA2 = 0; } while(0)
#define JSDO_Toggle()             do { LATAbits.LATA2 = ~LATAbits.LATA2; } while(0)
#define JSDO_GetValue()           PORTAbits.RA2
#define JSDO_SetDigitalInput()    do { TRISAbits.TRISA2 = 1; } while(0)
#define JSDO_SetDigitalOutput()   do { TRISAbits.TRISA2 = 0; } while(0)
#define JSDO_SetPullup()          do { WPUAbits.WPUA2 = 1; } while(0)
#define JSDO_ResetPullup()        do { WPUAbits.WPUA2 = 0; } while(0)
#define JSDO_SetPushPull()        do { ODCONAbits.ODCA2 = 0; } while(0)
#define JSDO_SetOpenDrain()       do { ODCONAbits.ODCA2 = 1; } while(0)
#define JSDO_SetAnalogMode()      do { ANSELAbits.ANSA2 = 1; } while(0)
#define JSDO_SetDigitalMode()     do { ANSELAbits.ANSA2 = 0; } while(0)

// get/set USER2 aliases
#define USER2_TRIS                 TRISAbits.TRISA4
#define USER2_LAT                  LATAbits.LATA4
#define USER2_PORT                 PORTAbits.RA4
#define USER2_WPU                  WPUAbits.WPUA4
#define USER2_OD                   ODCONAbits.ODCA4
#define USER2_ANS                  ANSELAbits.ANSA4
#define USER2_SetHigh()            do { LATAbits.LATA4 = 1; } while(0)
#define USER2_SetLow()             do { LATAbits.LATA4 = 0; } while(0)
#define USER2_Toggle()             do { LATAbits.LATA4 = ~LATAbits.LATA4; } while(0)
#define USER2_GetValue()           PORTAbits.RA4
#define USER2_SetDigitalInput()    do { TRISAbits.TRISA4 = 1; } while(0)
#define USER2_SetDigitalOutput()   do { TRISAbits.TRISA4 = 0; } while(0)
#define USER2_SetPullup()          do { WPUAbits.WPUA4 = 1; } while(0)
#define USER2_ResetPullup()        do { WPUAbits.WPUA4 = 0; } while(0)
#define USER2_SetPushPull()        do { ODCONAbits.ODCA4 = 0; } while(0)
#define USER2_SetOpenDrain()       do { ODCONAbits.ODCA4 = 1; } while(0)
#define USER2_SetAnalogMode()      do { ANSELAbits.ANSA4 = 1; } while(0)
#define USER2_SetDigitalMode()     do { ANSELAbits.ANSA4 = 0; } while(0)

// get/set POWER_EN aliases
#define POWER_EN_TRIS                 TRISAbits.TRISA5
#define POWER_EN_LAT                  LATAbits.LATA5
#define POWER_EN_PORT                 PORTAbits.RA5
#define POWER_EN_WPU                  WPUAbits.WPUA5
#define POWER_EN_OD                   ODCONAbits.ODCA5
#define POWER_EN_ANS                  ANSELAbits.ANSA5
#define POWER_EN_SetHigh()            do { LATAbits.LATA5 = 1; } while(0)
#define POWER_EN_SetLow()             do { LATAbits.LATA5 = 0; } while(0)
#define POWER_EN_Toggle()             do { LATAbits.LATA5 = ~LATAbits.LATA5; } while(0)
#define POWER_EN_GetValue()           PORTAbits.RA5
#define POWER_EN_SetDigitalInput()    do { TRISAbits.TRISA5 = 1; } while(0)
#define POWER_EN_SetDigitalOutput()   do { TRISAbits.TRISA5 = 0; } while(0)
#define POWER_EN_SetPullup()          do { WPUAbits.WPUA5 = 1; } while(0)
#define POWER_EN_ResetPullup()        do { WPUAbits.WPUA5 = 0; } while(0)
#define POWER_EN_SetPushPull()        do { ODCONAbits.ODCA5 = 0; } while(0)
#define POWER_EN_SetOpenDrain()       do { ODCONAbits.ODCA5 = 1; } while(0)
#define POWER_EN_SetAnalogMode()      do { ANSELAbits.ANSA5 = 1; } while(0)
#define POWER_EN_SetDigitalMode()     do { ANSELAbits.ANSA5 = 0; } while(0)

// get/set BLUE aliases
#define BLUE_TRIS                 TRISBbits.TRISB4
#define BLUE_LAT                  LATBbits.LATB4
#define BLUE_PORT                 PORTBbits.RB4
#define BLUE_WPU                  WPUBbits.WPUB4
#define BLUE_OD                   ODCONBbits.ODCB4
#define BLUE_ANS                  ANSELBbits.ANSB4
#define BLUE_SetHigh()            do { LATBbits.LATB4 = 1; } while(0)
#define BLUE_SetLow()             do { LATBbits.LATB4 = 0; } while(0)
#define BLUE_Toggle()             do { LATBbits.LATB4 = ~LATBbits.LATB4; } while(0)
#define BLUE_GetValue()           PORTBbits.RB4
#define BLUE_SetDigitalInput()    do { TRISBbits.TRISB4 = 1; } while(0)
#define BLUE_SetDigitalOutput()   do { TRISBbits.TRISB4 = 0; } while(0)
#define BLUE_SetPullup()          do { WPUBbits.WPUB4 = 1; } while(0)
#define BLUE_ResetPullup()        do { WPUBbits.WPUB4 = 0; } while(0)
#define BLUE_SetPushPull()        do { ODCONBbits.ODCB4 = 0; } while(0)
#define BLUE_SetOpenDrain()       do { ODCONBbits.ODCB4 = 1; } while(0)
#define BLUE_SetAnalogMode()      do { ANSELBbits.ANSB4 = 1; } while(0)
#define BLUE_SetDigitalMode()     do { ANSELBbits.ANSB4 = 0; } while(0)

// get/set GREEN aliases
#define GREEN_TRIS                 TRISBbits.TRISB5
#define GREEN_LAT                  LATBbits.LATB5
#define GREEN_PORT                 PORTBbits.RB5
#define GREEN_WPU                  WPUBbits.WPUB5
#define GREEN_OD                   ODCONBbits.ODCB5
#define GREEN_ANS                  ANSELBbits.ANSB5
#define GREEN_SetHigh()            do { LATBbits.LATB5 = 1; } while(0)
#define GREEN_SetLow()             do { LATBbits.LATB5 = 0; } while(0)
#define GREEN_Toggle()             do { LATBbits.LATB5 = ~LATBbits.LATB5; } while(0)
#define GREEN_GetValue()           PORTBbits.RB5
#define GREEN_SetDigitalInput()    do { TRISBbits.TRISB5 = 1; } while(0)
#define GREEN_SetDigitalOutput()   do { TRISBbits.TRISB5 = 0; } while(0)
#define GREEN_SetPullup()          do { WPUBbits.WPUB5 = 1; } while(0)
#define GREEN_ResetPullup()        do { WPUBbits.WPUB5 = 0; } while(0)
#define GREEN_SetPushPull()        do { ODCONBbits.ODCB5 = 0; } while(0)
#define GREEN_SetOpenDrain()       do { ODCONBbits.ODCB5 = 1; } while(0)
#define GREEN_SetAnalogMode()      do { ANSELBbits.ANSB5 = 1; } while(0)
#define GREEN_SetDigitalMode()     do { ANSELBbits.ANSB5 = 0; } while(0)

// get/set RED aliases
#define RED_TRIS                 TRISBbits.TRISB6
#define RED_LAT                  LATBbits.LATB6
#define RED_PORT                 PORTBbits.RB6
#define RED_WPU                  WPUBbits.WPUB6
#define RED_OD                   ODCONBbits.ODCB6
#define RED_ANS                  ANSELBbits.ANSB6
#define RED_SetHigh()            do { LATBbits.LATB6 = 1; } while(0)
#define RED_SetLow()             do { LATBbits.LATB6 = 0; } while(0)
#define RED_Toggle()             do { LATBbits.LATB6 = ~LATBbits.LATB6; } while(0)
#define RED_GetValue()           PORTBbits.RB6
#define RED_SetDigitalInput()    do { TRISBbits.TRISB6 = 1; } while(0)
#define RED_SetDigitalOutput()   do { TRISBbits.TRISB6 = 0; } while(0)
#define RED_SetPullup()          do { WPUBbits.WPUB6 = 1; } while(0)
#define RED_ResetPullup()        do { WPUBbits.WPUB6 = 0; } while(0)
#define RED_SetPushPull()        do { ODCONBbits.ODCB6 = 0; } while(0)
#define RED_SetOpenDrain()       do { ODCONBbits.ODCB6 = 1; } while(0)
#define RED_SetAnalogMode()      do { ANSELBbits.ANSB6 = 1; } while(0)
#define RED_SetDigitalMode()     do { ANSELBbits.ANSB6 = 0; } while(0)

// get/set USER1 aliases
#define USER1_TRIS                 TRISBbits.TRISB7
#define USER1_LAT                  LATBbits.LATB7
#define USER1_PORT                 PORTBbits.RB7
#define USER1_WPU                  WPUBbits.WPUB7
#define USER1_OD                   ODCONBbits.ODCB7
#define USER1_ANS                  ANSELBbits.ANSB7
#define USER1_SetHigh()            do { LATBbits.LATB7 = 1; } while(0)
#define USER1_SetLow()             do { LATBbits.LATB7 = 0; } while(0)
#define USER1_Toggle()             do { LATBbits.LATB7 = ~LATBbits.LATB7; } while(0)
#define USER1_GetValue()           PORTBbits.RB7
#define USER1_SetDigitalInput()    do { TRISBbits.TRISB7 = 1; } while(0)
#define USER1_SetDigitalOutput()   do { TRISBbits.TRISB7 = 0; } while(0)
#define USER1_SetPullup()          do { WPUBbits.WPUB7 = 1; } while(0)
#define USER1_ResetPullup()        do { WPUBbits.WPUB7 = 0; } while(0)
#define USER1_SetPushPull()        do { ODCONBbits.ODCB7 = 0; } while(0)
#define USER1_SetOpenDrain()       do { ODCONBbits.ODCB7 = 1; } while(0)
#define USER1_SetAnalogMode()      do { ANSELBbits.ANSB7 = 1; } while(0)
#define USER1_SetDigitalMode()     do { ANSELBbits.ANSB7 = 0; } while(0)
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

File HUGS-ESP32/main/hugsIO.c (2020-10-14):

/*
 * hugs.c
 *
 *  Created on: Mar 20, 2020
 *      Author: Phil
 */

#include <stdlib.h>
#include <time.h>
#include <string.h>
#include <assert.h>
#include "freertos/FreeRTOS.h"
#include "freertos/semphr.h"
#include "freertos/timers.h"
#include "nvs_flash.h"
#include "esp_event.h"
#include "esp_netif.h"
#include "esp_wifi.h"
#include "esp_log.h"
#include "esp_system.h"
#include "driver/gpio.h"

#include "hugs.h"
#include "hugsIO.h"

#define CYCLES_PER_SEC   20
#define FWD_PIN	19
#define REV_PIN 21
#define LFT_PIN 22
#define RIG_PIN 23
#define PIN_SEL   ((1ULL << FWD_PIN) | (1ULL << REV_PIN) | (1ULL << LFT_PIN) | (1ULL << RIG_PIN))

#define TOP_AXIAL_SPEED 230
#define TOP_YAW_SPEED    60
#define TOP_SWEEP_SPEED  20

#define SHIFT_BITS      2
#define AXIAL_ACC_LIMIT 300      //  mm/s/s
#define YAW_ACC_LIMIT   45       //  deg/s/s
#define SWEEP_ACC_LIMIT 30       //  deg/s/s

static void driving(void *pvParameter);

int16_t     targetAxialFP = 0;
int16_t     targetYawFP   = 0;

int16_t     limitedAxialFP = 0;
int16_t     limitedYawFP   = 0;

int16_t     accelAxialFP = 0;
int16_t     accelYawFP   = 0;

int16_t     accelLimitAxialFP   = (AXIAL_ACC_LIMIT << SHIFT_BITS) / CYCLES_PER_SEC ;
int16_t     accelLimitYawFP     = (YAW_ACC_LIMIT   << SHIFT_BITS) / CYCLES_PER_SEC ;
int16_t     accelLimitSweepFP   = (SWEEP_ACC_LIMIT << SHIFT_BITS) / CYCLES_PER_SEC ;

int16_t     topAxialSpeedFP   = (TOP_AXIAL_SPEED << SHIFT_BITS) ;
int16_t     topYawSpeedFP     = (TOP_YAW_SPEED   << SHIFT_BITS) ;
int16_t     topSweepSpeedFP   = (TOP_SWEEP_SPEED << SHIFT_BITS) ;

TickType_t PostPeriod = (1000 / CYCLES_PER_SEC) / portTICK_PERIOD_MS;

bool	goFwd;
bool	goRev;
bool	goLft;
bool	goRig;

void	start_HUGSIO_tasks(){
    // Configure IO Pins
    gpio_config_t io_conf;

	// Setup inputs
    targetAxialFP = 0;
    targetYawFP   = 0;
    limitedAxialFP = 0;
    limitedYawFP   = 0;

	// Pull-up Button pins
    io_conf.intr_type = GPIO_PIN_INTR_DISABLE;
    io_conf.mode = GPIO_MODE_INPUT;
    io_conf.pin_bit_mask = PIN_SEL;
    io_conf.pull_down_en = 0;
    io_conf.pull_up_en = 1;
    gpio_config(&io_conf);

	// Create polling task.
    xTaskCreate(&driving, "driving task", 2048, NULL, 6, NULL);
}

static void driving(void *pvParameter)
{
    TickType_t 	xLastWakeTime;

    // Initialize the xLastWakeTime variable with the current time.
    resetPosition();
    setSpeedMode(SPEED_PF, 200);
    xLastWakeTime = xTaskGetTickCount();

    while(1) {
    	// Wait one full post cycle
        vTaskDelayUntil( &xLastWakeTime, PostPeriod );

        goFwd =	(gpio_get_level(FWD_PIN) == 0);
        goRev =	(gpio_get_level(REV_PIN) == 0);
        goLft =	(gpio_get_level(LFT_PIN) == 0);
        goRig =	(gpio_get_level(RIG_PIN) == 0);

        // Use the joystick buttons to set the target speeds
        accelAxialFP = accelLimitAxialFP;
        accelYawFP   = accelLimitYawFP;

        if (goFwd)
            targetAxialFP =  topAxialSpeedFP;
        else if (goRev)
            targetAxialFP = -topAxialSpeedFP;
        else
            targetAxialFP =   0;

        if (goRig){
            if (targetAxialFP == 0)
                targetYawFP =  topYawSpeedFP;
            else {
                targetYawFP =  topSweepSpeedFP;
                accelYawFP   = accelLimitSweepFP;
            }
        }
        else if (goLft){
            if (targetAxialFP == 0)
                targetYawFP =  -topYawSpeedFP;
            else {
                targetYawFP =  -topSweepSpeedFP;
                accelYawFP   = accelLimitSweepFP;
            }
        }
        else
            targetYawFP =   0;
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

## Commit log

2020-08-14 Added Cad models for HB 1/4 20 Mounting
    [HOVER-disk-b.dxf, HOVER-disk-b.ipt, HOVER-plate-b.ipt, HOVER_plate-b.dxf]
2020-09-02 Updated Pairing
    New LED colors
    Clearing Bluetooth IDs during Pairing
2020-10-05 Hackaday Prize Release.
    Latest Firmware, Software, PCB and Cad.
    [BluJoy-2.1.brd, BluJoy-2.1.sch, BluJoy-e.sch, copper_bottom.gbr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]
2020-10-14 Added HUGS-ESP32 firmware to Repo.
    HUGS-ESP32 was used for development and testing of the Hoverboard Firmware, but has been superceeded by the opperational BluJoy code.
    [HUGS Protocol Doc.xlsx]
2021-06-13 Added single serial port interface
    Added serial processing on debug Coms port.
    Accepts new Dual Speed command DSPE For left and right motor.
2021-06-13 Updated GigaDevice Libraries (3.2)
    [CommunicationOverview.xlsx, HUGS Protocol Doc.xlsx]

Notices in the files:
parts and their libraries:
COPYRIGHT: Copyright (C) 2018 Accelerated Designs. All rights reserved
